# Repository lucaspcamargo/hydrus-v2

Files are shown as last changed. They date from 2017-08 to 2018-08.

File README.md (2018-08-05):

# Hydrus v2

Hydrus is an autonomous surface vehicle for water quality measurement. The original v1 platform won **first place at the Intel Embedded Systems Competition 2016**. This repository contains v2: a ground-up retool of the vehicle firmware and hardware, now running on a **Raspberry Pi Zero W** atop a custom backbone board.

The vehicle navigates a body of water along a pre-planned route, stops at designated waypoints to collect sensor readings, and streams data in real time to a Qt5-based base station running on a laptop.

The project spans embedded firmware, base station software, custom PCB hardware design, and 3D-printed mechanical components.

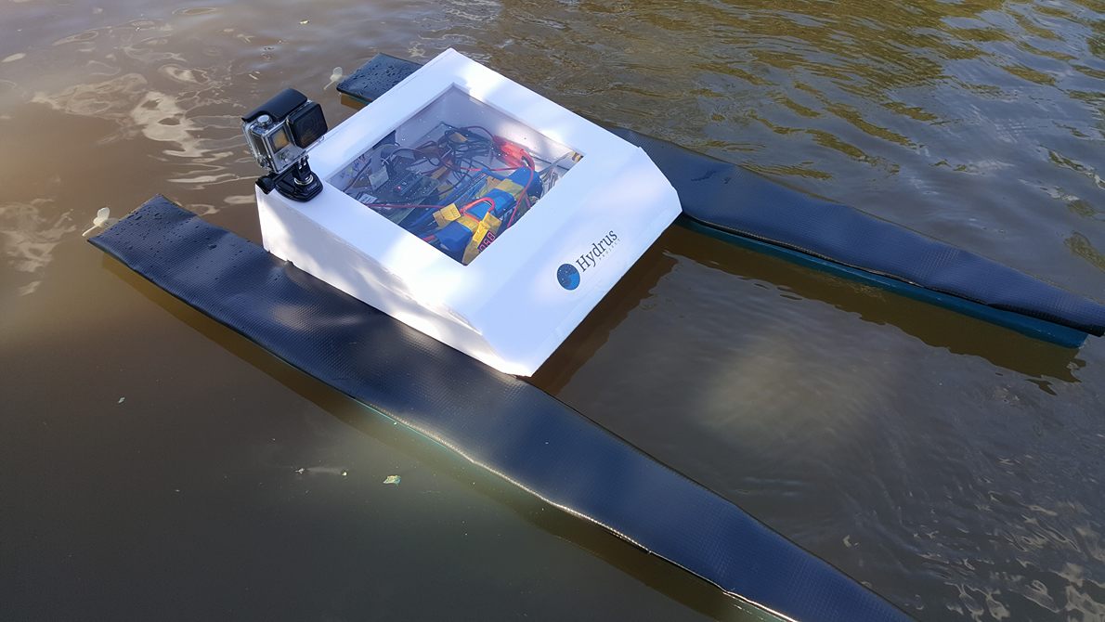
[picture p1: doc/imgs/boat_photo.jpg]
Hydrus on the water


`Hydrus during field testing on a lake in Joinville, 2016.`

## Hardware

The vehicle runs on a Raspberry Pi Zero W with a custom backbone board that integrates all peripherals:

- **GPS**: u-blox NEO-6 for position and speed
- **IMU**: HMC5883L 3-axis magnetometer for heading
- **ADC**: ADS1115 16-bit I2C ADC multiplexing four analog channels
- **Water sensors**: pH probe, TMP36 temperature sensor, TSD-10 turbidity sensor
- **Propulsion**: dual brushed motors with PWM speed control (differential drive)
- **Power**: LiPo battery with voltage monitoring

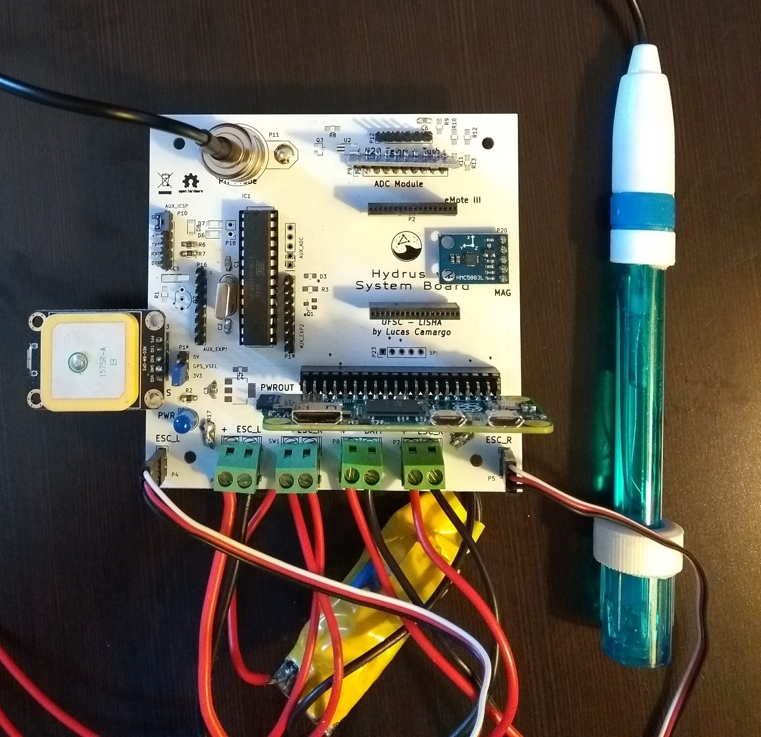
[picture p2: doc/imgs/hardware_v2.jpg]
Custom Hydrus System Board with GPS antenna and pH probe


`The custom Hydrus v2 System Board, with GPS antenna and pH probe.`

Hardware design files (KiCad schematics and layouts) are in `hw/`. Mechanical parts (propellers, axle adapters, board mounts) are 3D-printable models in `mech/`.

## Firmware

The vehicle firmware (`fw/`) is written in C++11 and built with CMake. It runs four concurrent periodic tasks:

| Task | Rate | Responsibility |
|------|------|----------------|
| `SystemTask` | 2 Hz | State machine, battery/thermal monitoring, shutdown |
| `SensingTask` | 30 Hz | pH, temperature, turbidity, IMU heading |
| `NavigationTask` | 10 Hz | GPS, motor control, waypoint tracking |
| `CommTask` | 20 Hz | TCP link to base station, command routing |

All tasks share a **double-buffered blackboard** with reader-writer locking, which eliminates contention between producers and consumers without blocking.

### Navigation

Autonomous navigation follows a state machine: align to bearing → traverse toward waypoint → acquire data → advance to next waypoint. Distance and bearing use the Haversine formula and forward azimuth calculation against WGS-84 coordinates. Speed is throttled adaptively as the vehicle closes in on a waypoint.

A remote-control mode is also supported, accepting velocity vectors from the base station for manual operation.

## Base Station

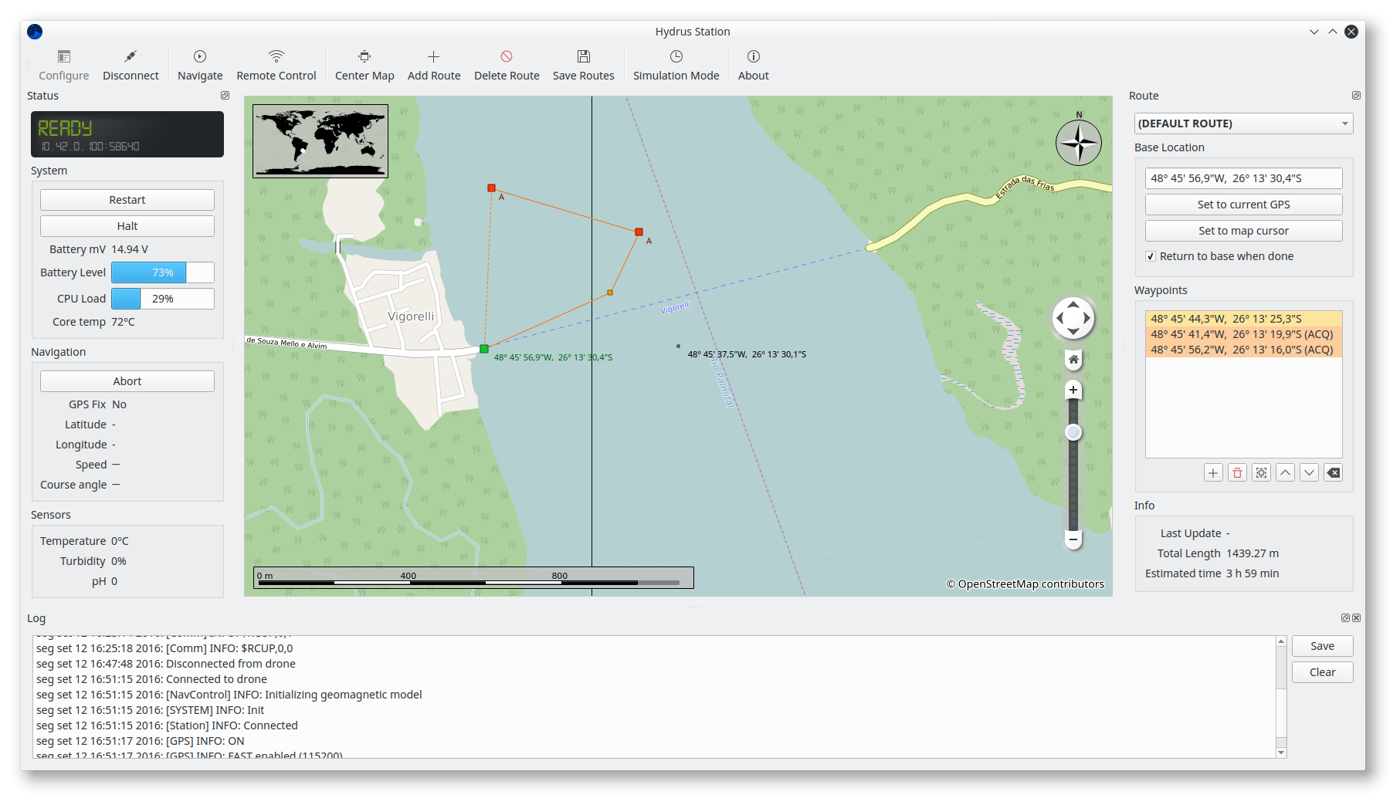
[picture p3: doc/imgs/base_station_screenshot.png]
Base station software showing a live mission on the map


`Base station software showing a live mission on the map.`

The base station (`station/`) is a Qt5/C++ desktop application featuring:

- **Live map** via the Marble widget, showing vehicle position, heading, trail, and waypoints over OpenStreetMap tiles
- **Route editor** for building multi-waypoint missions with per-waypoint acquire flags
- **Real-time dashboard** for sensor readings, system state, and battery level
- **Log viewer** with streaming from the vehicle and timeline-based replay
- **RC control widget** with joystick/gamepad support

Communication uses a TCP socket (port 6666). The vehicle streams binary blackboard snapshots and log messages; the base station sends text commands.

## Repository layout

```
doc/      Documentation and branding (including competition presentation)
fw/       Vehicle firmware (C++11, CMake)
lib/      Shared libraries
station/  Base station software (Qt5, C++11)
hw/       PCB schematics and layouts (KiCad)
mech/     3D-printable mechanical components
```

## Credits

The original Hydrus project was developed at Universidade Federal de Santa Catarina. Team members: Guilherme Augusto Pangratz and Emili Bohrer. Mentored by Prof. Dr. Giovani Gracioli.

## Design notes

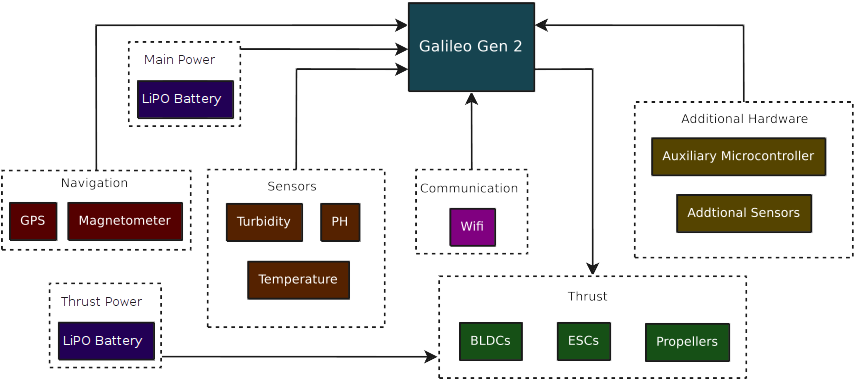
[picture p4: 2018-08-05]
doc/imgs/v1_hardware_blocks.png

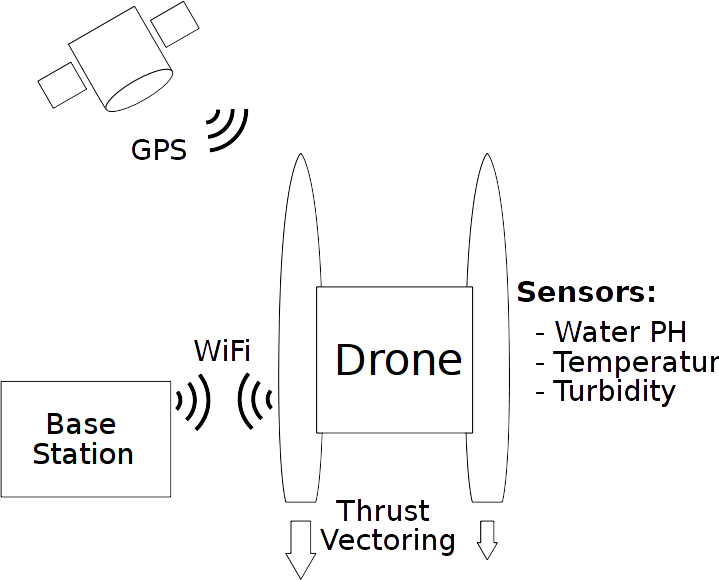
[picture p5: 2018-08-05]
doc/imgs/concept.png

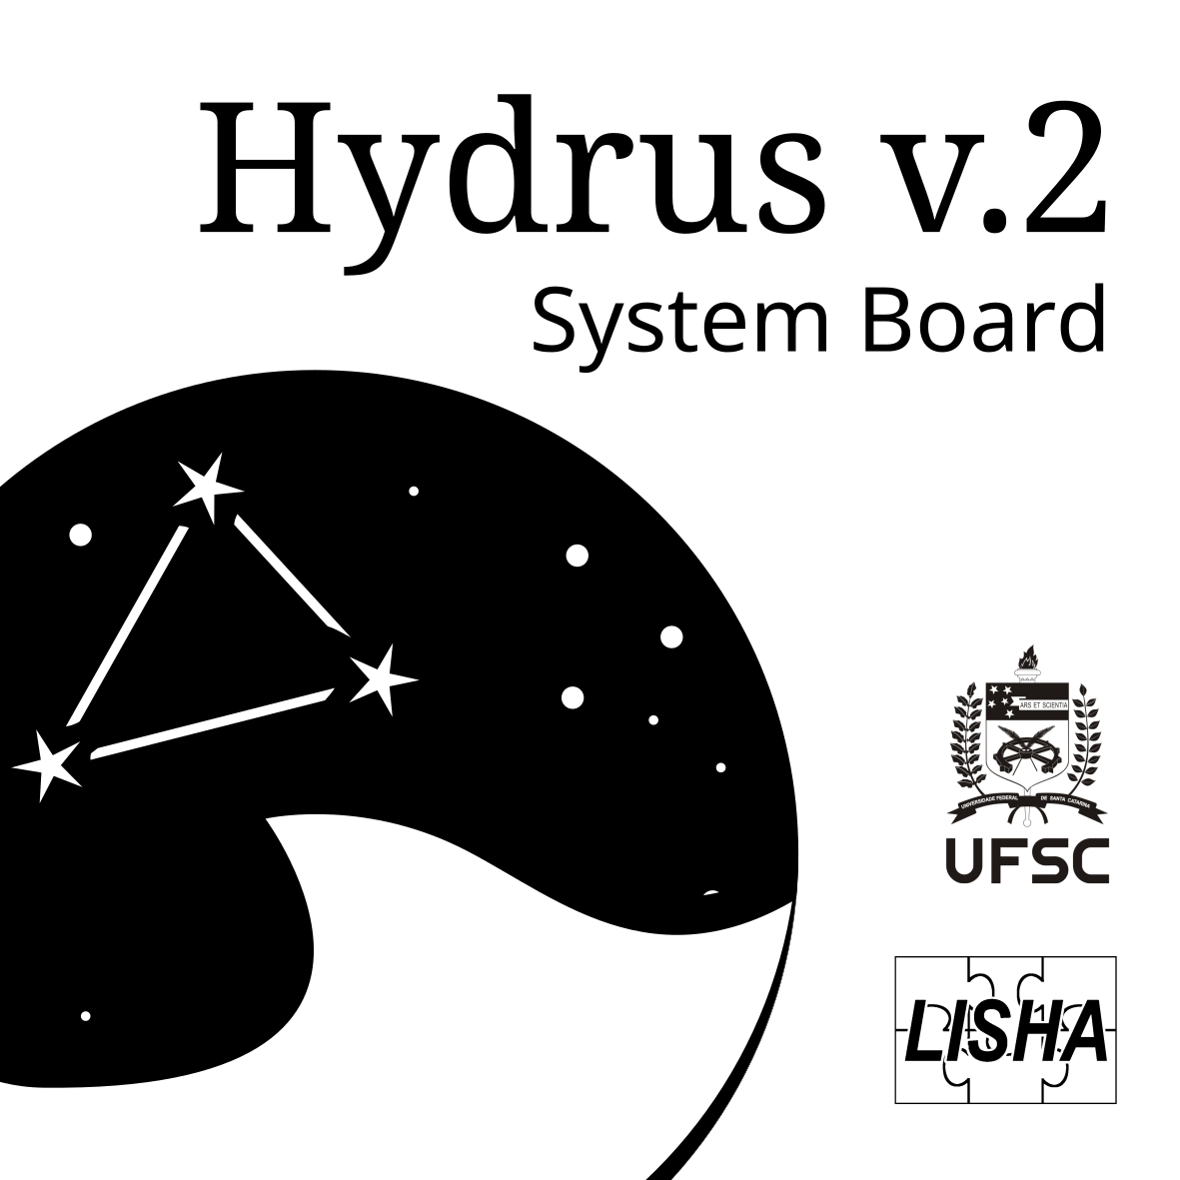
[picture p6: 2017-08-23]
doc/branding/board-backside.png

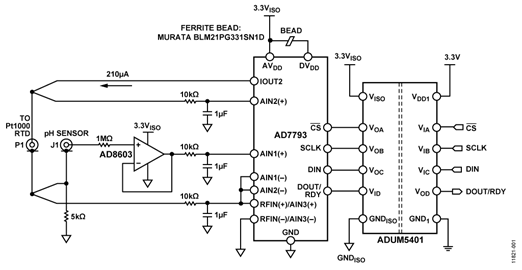
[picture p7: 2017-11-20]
hw/datasheets/ph-buffer-reference.png

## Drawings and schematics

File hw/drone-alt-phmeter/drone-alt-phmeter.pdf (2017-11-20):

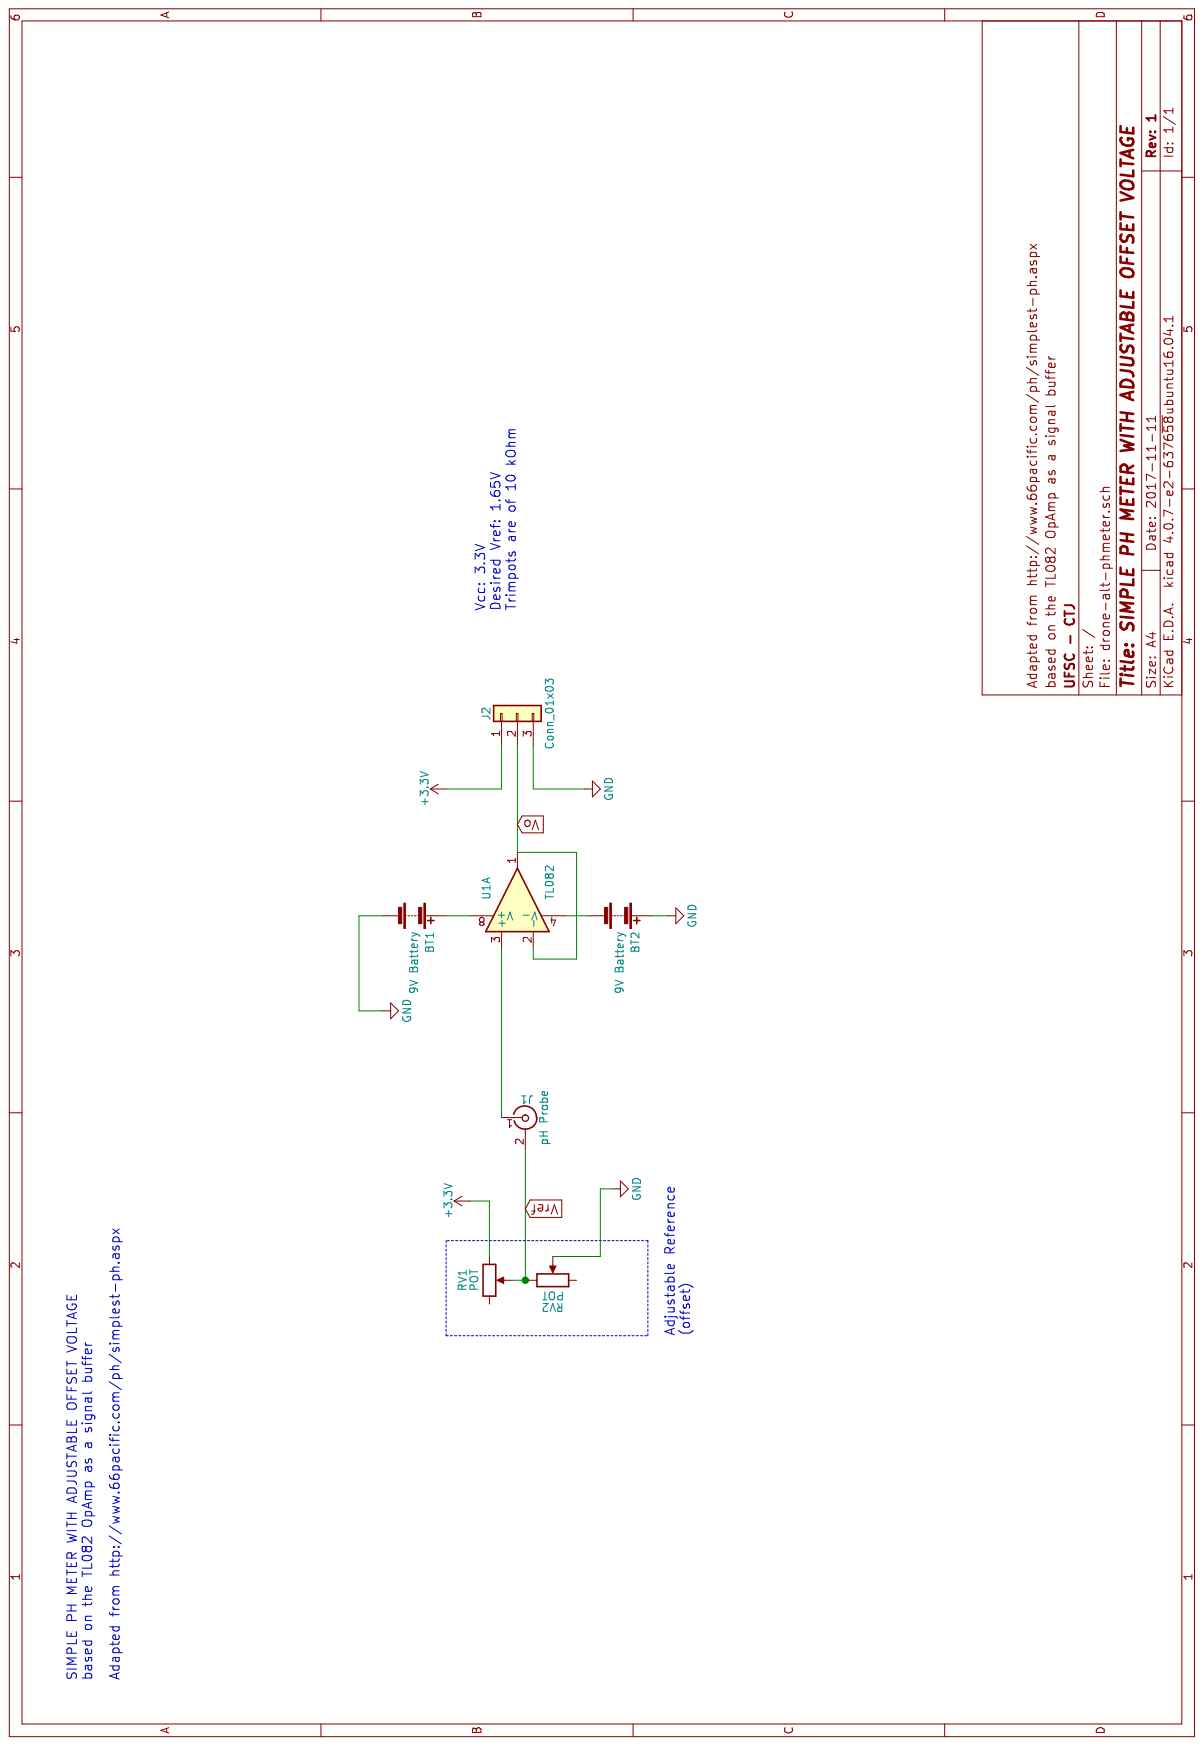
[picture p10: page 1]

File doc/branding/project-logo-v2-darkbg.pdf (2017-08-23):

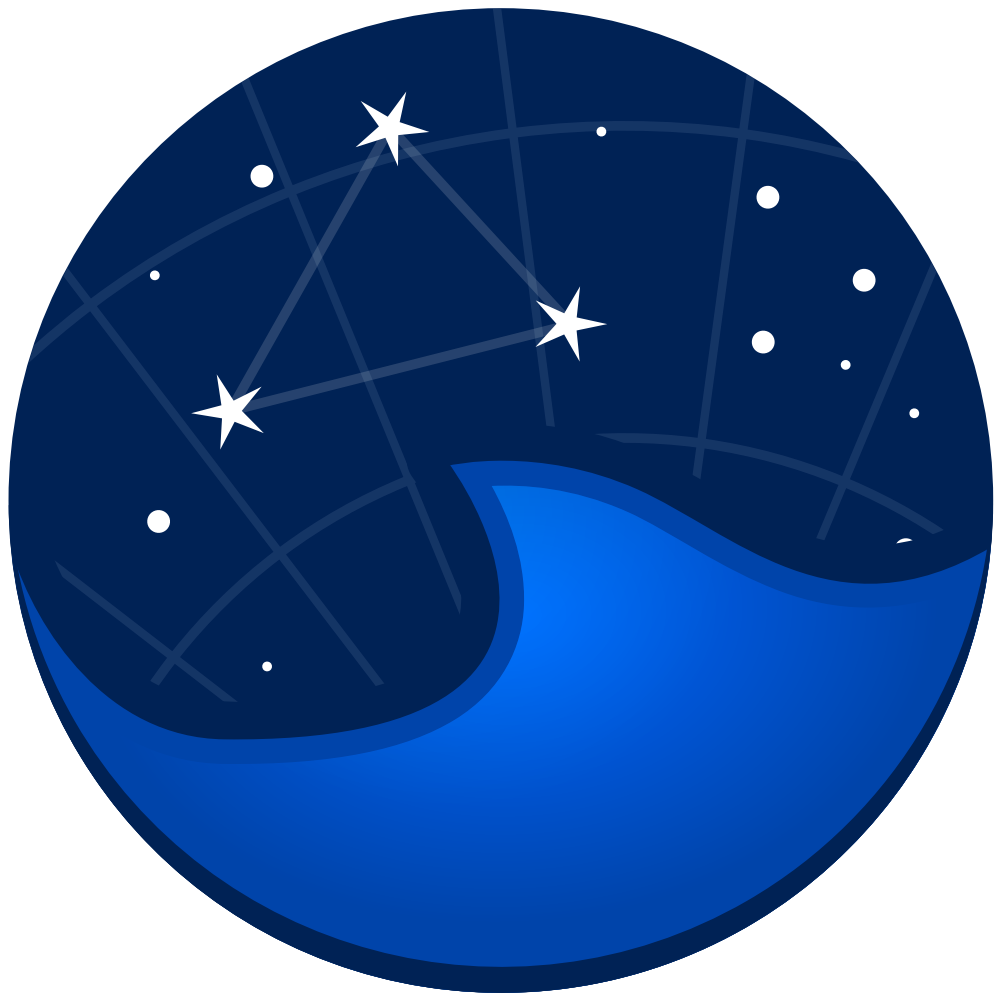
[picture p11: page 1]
Hydrus P R O J E C T

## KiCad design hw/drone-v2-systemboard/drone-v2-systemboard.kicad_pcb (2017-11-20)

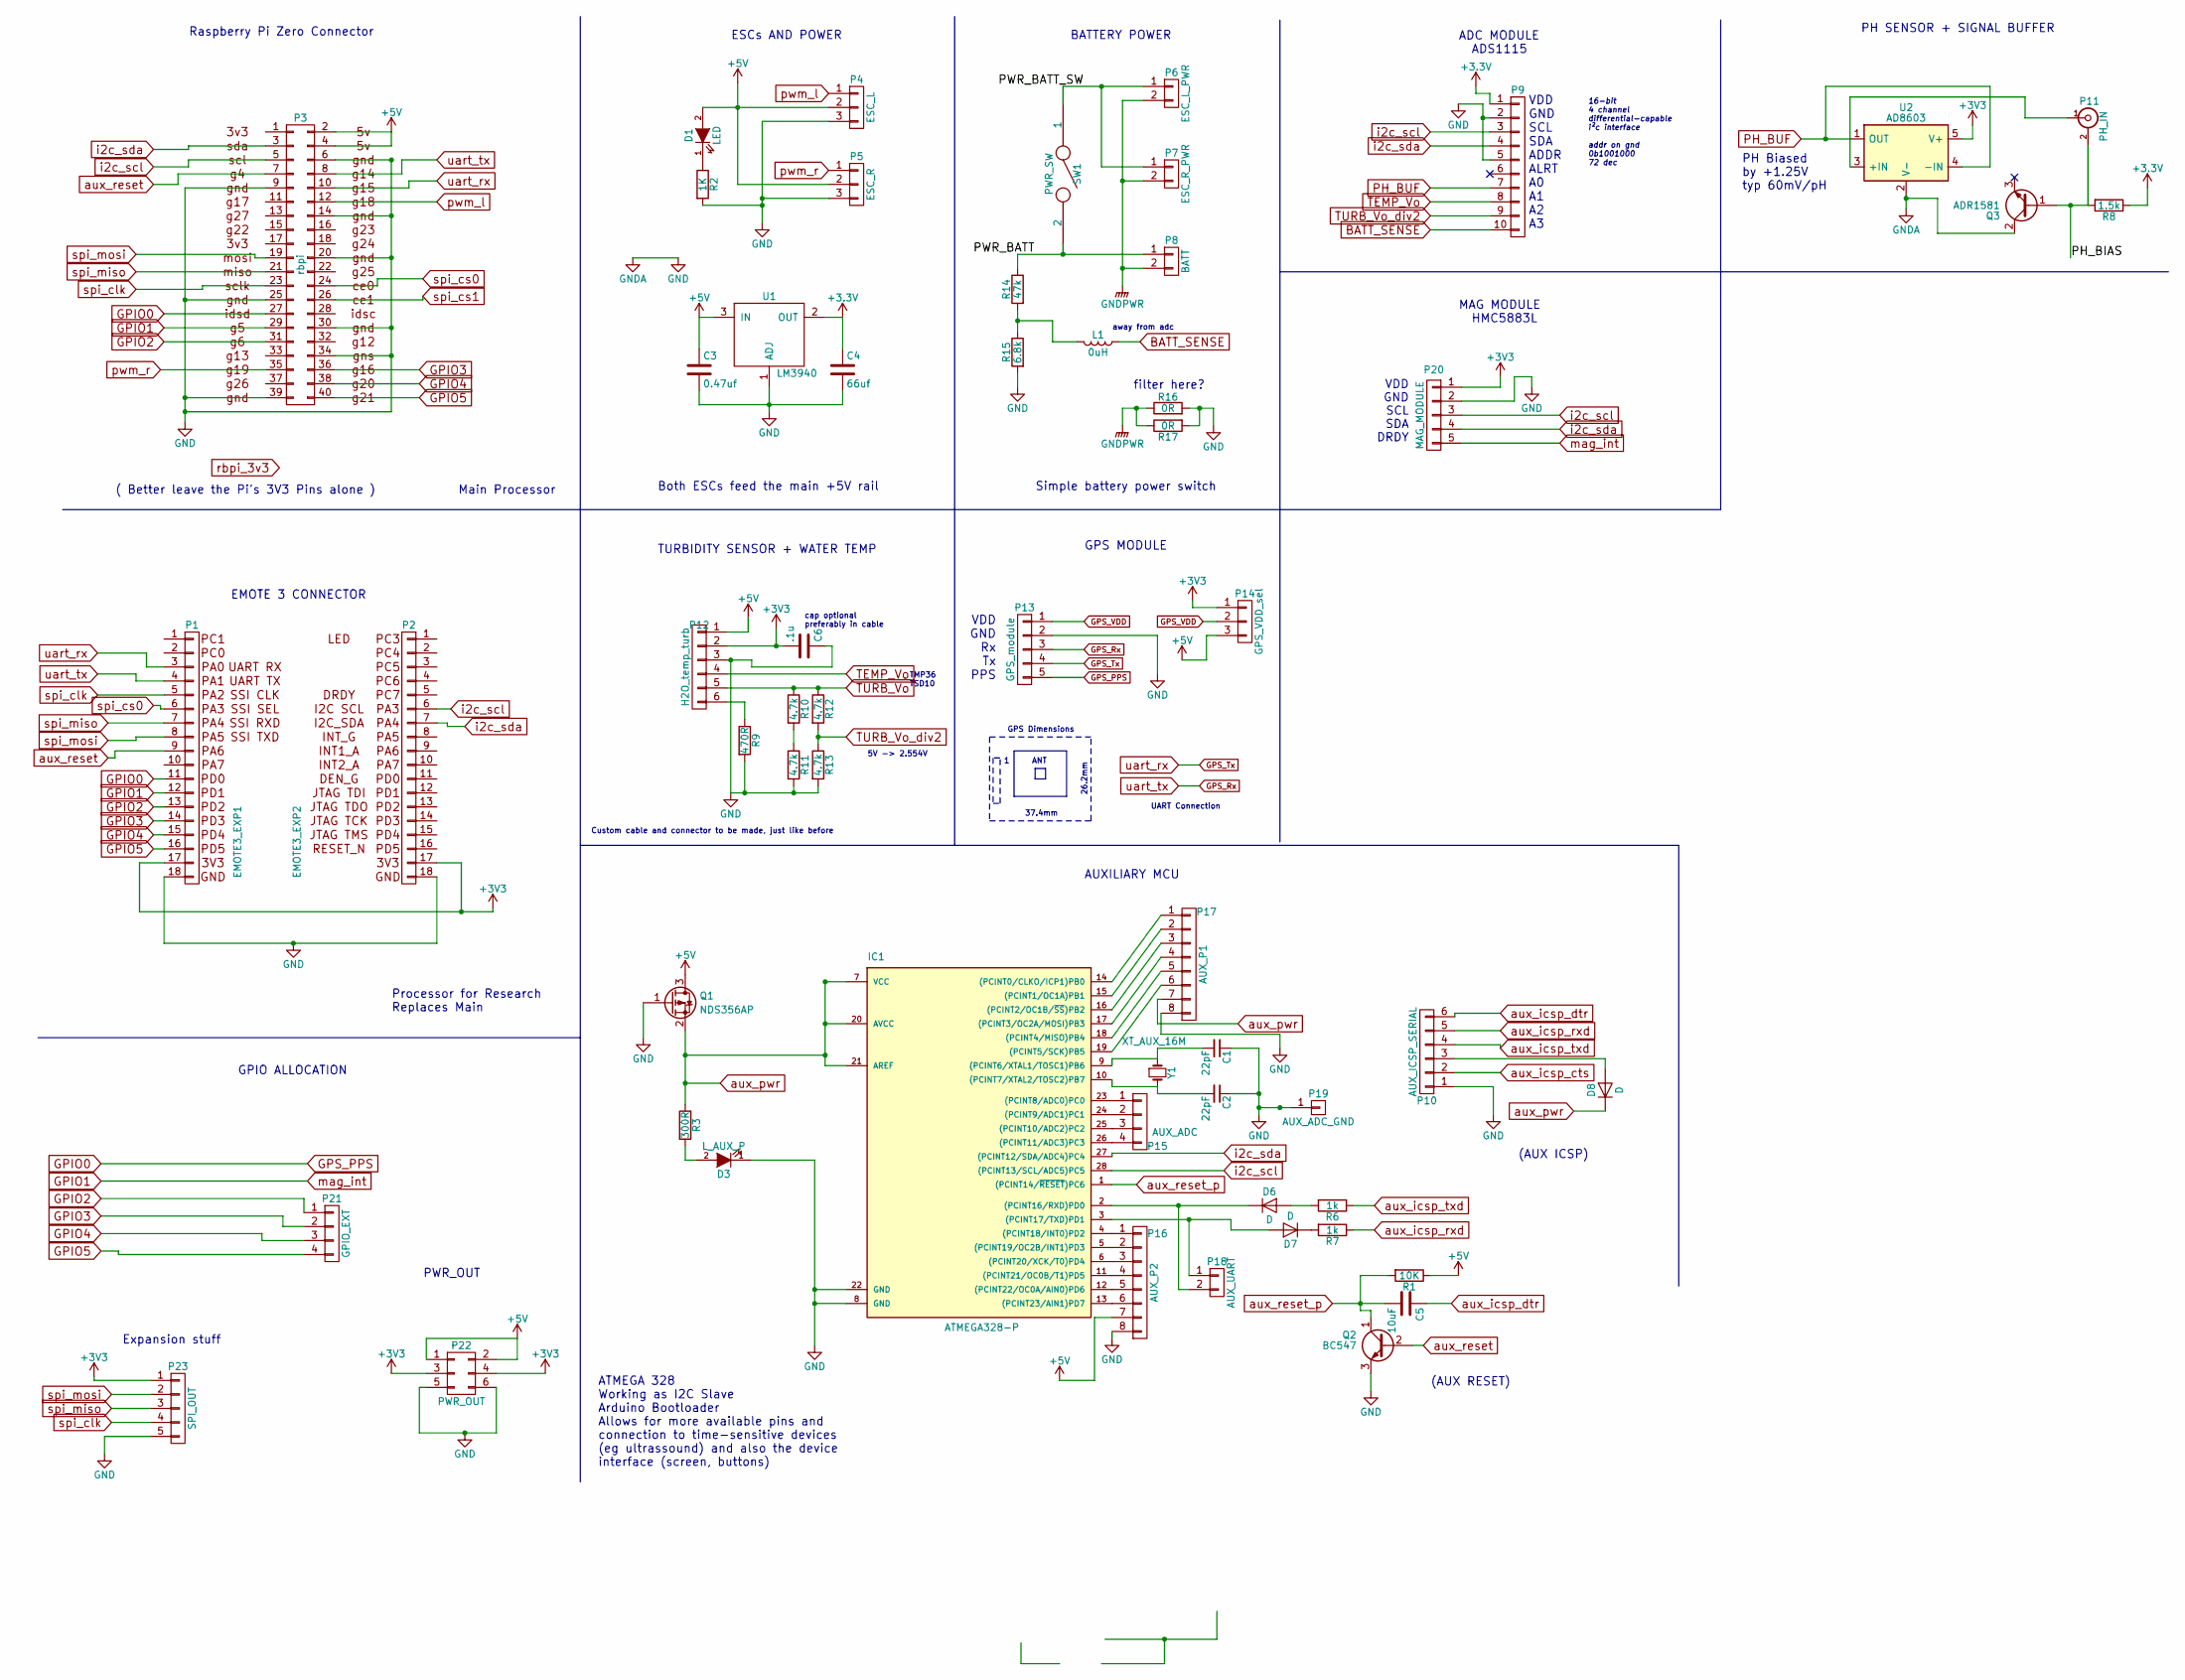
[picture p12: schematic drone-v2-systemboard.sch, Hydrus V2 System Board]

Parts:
C1, C2: 22pF; C_0805_HandSoldering
C3: 0.47uf; C_0805_HandSoldering
C4: 66uf; C_0805_HandSoldering
C5: 10uF; CP_Tantalum_Case-S_EIA-3216-12_Hand
C6: .1u; C_0805_HandSoldering
D1: LED; LED-5MM
D3: L_AUX_P; LED_0805
D6, D7, D8: D; D_SOD-123
IC1: ATMEGA328-P; DIP-28_W7.62mm
L1: 0uH; Inductor_1212
P1: EMOTE3_EXP1; HEADER_18x1_EMOTE
P2: EMOTE3_EXP2; HEADER_18x1_EMOTE
P3: rbpi; Pin_Header_Straight_2x20
P4: ESC_L; Pin_Header_Straight_1x03
P5: ESC_R; Pin_Header_Straight_1x03
P6: ESC_L_PWR; AK300-2
P7: ESC_R_PWR; AK300-2
P8: BATT; AK300-2
P9: ADC_MODULE; Pin_Header_Straight_1x10_Pitch2.54mm
P10: AUX_ICSP_SERIAL; Pin_Header_Straight_1x06_Pitch2.54mm
P11: PH_IN; BNC
P12: H2O_temp_turb; Pin_Header_Straight_1x06_Pitch2.54mm
P13: GPS_module; Pin_Header_Straight_1x05_Pitch2.54mm
P14: GPS_VDD_sel; Pin_Header_Straight_1x03_Pitch2.54mm
P15: AUX_ADC; Pin_Header_Straight_1x04_Pitch2.54mm
P16: AUX_P2; Pin_Header_Straight_1x08_Pitch2.54mm
P17: AUX_P1; Pin_Header_Straight_1x08_Pitch2.54mm
P18: AUX_UART; Pin_Header_Straight_1x02_Pitch2.54mm
P19: AUX_ADC_GND; Pin_Header_Straight_1x01_Pitch2.54mm
P20: MAG_MODULE; Pin_Header_Straight_1x05_Pitch2.54mm
P21: GPIO_EXT; Pin_Header_Straight_1x04_Pitch2.54mm
P22: PWR_OUT; Pin_Header_Straight_2x03_Pitch2.54mm
P23: SPI_OUT; Pin_Header_Straight_1x05_Pitch2.54mm
Q1: NDS356AP; SuperSOT-3
Q2: BC547; TO-92_Inline_Wide
Q3: ADR1581; SOT-23
R1: 10K; R_0805_HandSoldering
R2: 1K; R_0805_HandSoldering
R3: 300R; R_0805_HandSoldering
R6, R7: 1k; R_0805_HandSoldering
R8: 1.5k; R_0805_HandSoldering
R9: 470R; R_0805_HandSoldering
R10, R11, R12, R13: 4.7k; R_0805_HandSoldering
R14: 47k; R_0805_HandSoldering
R15: 6.8k; R_0805_HandSoldering
R16, R17: 0R; R_1210_HandSoldering
SW1: PWR_SW; AK300-2
U1: LM3940; SOT-223-3Lead_TabPin2
U2: AD8603; TSOT-23-5_HandSoldering
Y1: XT_AUX_16M; Crystal_HC49-U_Vertical

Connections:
+5V: C3.1, D1.2 (A), P3.2, P3.4, P4.2, P5.2, P12.1, P14.3, P16.7, P22.1, P22.2, Q1.3 (D), R1.1, U1.3 (IN)
/PH_BIAS: P11.2 (Ext), Q3.1 (B), R8.2
/PWR_BATT: P8.1, R14.1, SW1.2
/PWR_BATT_SW: P6.1, P7.1, SW1.1
BATT_SENSE: L1.1, P9.10
GND: C1.1, C2.1, C3.2, C4.2, C6.1, D3.1 (K), IC1.8 (GND), IC1.22 (GND), P1.18, P2.18, P3.6, P3.9, P3.14, P3.20, P3.25, P3.30, P3.34, P3.39, P4.3, P5.3, P9.2, P9.5, P10.1, P12.3, P13.2, P16.8, P17.8, P19.1, P20.2, P22.5, P22.6, P23.5, Q1.1 (G), Q2.3 (E), Q3.2 (C), R2.2, R9.2, R11.2, R13.2, R15.2, R16.2, R17.2, U1.1 (ADJ), U2.2 (V-)
GNDPWR: P6.2, P7.2, P8.2, R16.1, R17.1
GPIO0: P1.11, P3.27, P13.5
GPIO1: P1.12, P3.29, P20.5
GPIO2: P1.13, P3.31, P21.1
GPIO3: P1.14, P3.36, P21.2
GPIO4: P1.15, P3.38, P21.3
GPIO5: P1.16, P3.40, P21.4
GPS_Rx: P1.4, P3.8, P13.3
GPS_Tx: P1.3, P3.10, P13.4
GPS_VDD: P13.1, P14.2
unnamed: C1.2, IC1.9 ((PCINT6/XTAL1/TOSC1)PB6), Y1.1
unnamed: C2.2, IC1.10 ((PCINT7/XTAL2/TOSC2)PB7), Y1.2
unnamed: D1.1 (K), R2.1
unnamed: D3.2 (A), R3.2
unnamed: D6.1 (K), IC1.2 ((PCINT16/RXD)PD0), P18.2
unnamed: D6.2 (A), R6.2
unnamed: D7.1 (K), R7.2
unnamed: D7.2 (A), IC1.3 ((PCINT17/TXD)PD1), P18.1
unnamed: D8.2 (A), P10.3
unnamed: IC1.4 ((PCINT18/INT0)PD2), P16.1
unnamed: IC1.5 ((PCINT19/OC2B/INT1)PD3), P16.2
unnamed: IC1.6 ((PCINT20/XCK/T0)PD4), P16.3
unnamed: IC1.11 ((PCINT21/OC0B/T1)PD5), P16.4
unnamed: IC1.12 ((PCINT22/OC0A/AIN0)PD6), P16.5
unnamed: IC1.13 ((PCINT23/AIN1)PD7), P16.6
unnamed: IC1.14 ((PCINT0/CLKO/ICP1)PB0), P17.1
unnamed: IC1.15 ((PCINT1/OC1A)PB1), P17.2
unnamed: IC1.16 ((PCINT2/OC1B/~SS~)PB2), P17.3
unnamed: IC1.17 ((PCINT3/OC2A/MOSI)PB3), P17.4
unnamed: IC1.18 ((PCINT4/MISO)PB4), P17.5
unnamed: IC1.19 ((PCINT5/SCK)PB5), P17.6
unnamed: IC1.23 ((PCINT8/ADC0)PC0), P15.1
unnamed: IC1.24 ((PCINT9/ADC1)PC1), P15.2
unnamed: IC1.25 ((PCINT10/ADC2)PC2), P15.3
unnamed: IC1.26 ((PCINT11/ADC3)PC3), P15.4
unnamed: L1.2, R14.2, R15.1
unnamed: P11.1 (In), U2.3 (+IN)
unnamed: P12.6, R9.1
unnamed: R10.2, R11.1
PH_BUF: P9.7, U2.1 (OUT), U2.4 (-IN)
TEMP_Vo: P9.8, P12.4
TURB_Vo: P12.5, R10.1, R12.1
TURB_Vo_div2: P9.9, R12.2, R13.1
aux_icsp_dtr: C5.1, P10.6
aux_icsp_rxd: P10.5, R7.1
aux_icsp_txd: P10.4, R6.1
aux_pwr: D8.1 (K), IC1.7 (VCC), IC1.20 (AVCC), IC1.21 (AREF), P17.7, Q1.2 (S), R3.1
aux_reset: P1.9, P3.7, Q2.2 (B)
aux_reset_p: C5.2, IC1.1 ((PCINT14/~RESET~)PC6), Q2.1 (C), R1.2
i2c_scl: IC1.28 ((PCINT13/SCL/ADC5)PC5), P2.6, P3.5, P9.3, P20.3
i2c_sda: IC1.27 ((PCINT12/SDA/ADC4)PC4), P2.7, P3.3, P9.4, P20.4
pwm_l: P3.12, P4.1
pwm_r: P3.35, P5.1
spi_clk: P1.5, P3.23, P23.4
spi_cs0: P1.6, P3.24
spi_miso: P1.7, P3.21, P23.3
spi_mosi: P1.8, P3.19, P23.2

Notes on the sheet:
EMOTE 3 CONNECTOR
Raspberry Pi Zero Connector
ESCs AND POWER
BATTERY POWER
AUXILIARY MCU
ADC MODULE ADS1115
(AUX RESET)
(AUX ICSP)
PH SENSOR + SIGNAL BUFFER
Both ESCs feed the main +5V rail
Simple battery power switch
TURBIDITY SENSOR + WATER TEMP
Main Processor
Processor for Research Replaces Main
PH Biased by +1.25V typ 60mV/pH
VDD GND SCL SDA ADDR ALRT A0 A1 A2 A3
16-bit 4 channel differential-capable i²c interface addr on gnd 0b1001000 72 dec
filter here?
away from adc
GPIO ALLOCATION
TMP36 TSD10
GPS MODULE
VDD GND Rx Tx PPS
26.2mm
37.4mm
ANT
GPS Dimensions
Custom cable and connector to be made, just like before
5V -> 2.554V
cap optional preferably in cable
VDD GND SCL SDA DRDY
MAG MODULE HMC5883L
ATMEGA 328 Working as I2C Slave Arduino Bootloader Allows for more available pins and connection to time-sensitive devices (eg ultrassound) and also the device interface (screen, buttons)
UART Connection
PWR_OUT
Expansion stuff
( Better leave the Pi's 3V3 Pins alone )

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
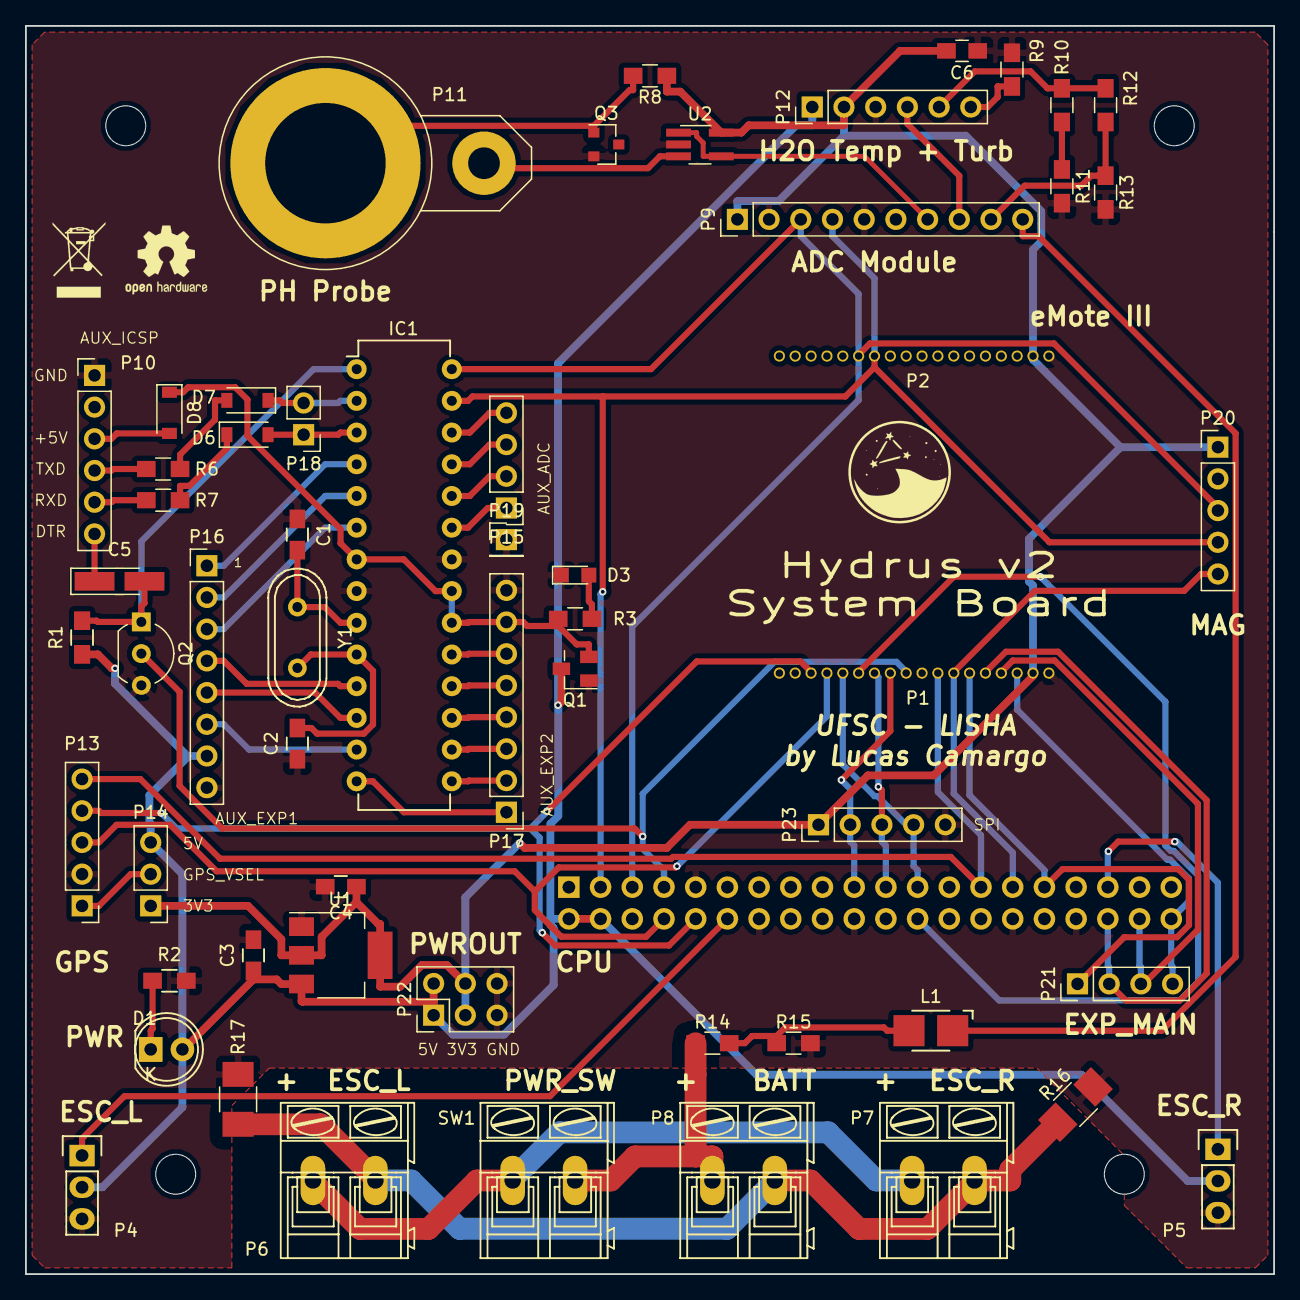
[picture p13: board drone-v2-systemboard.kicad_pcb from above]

Board: 2 copper layers, 100.0 x 100.0 mm, 64 parts (1 on the bottom side), 64 nets.

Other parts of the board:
HOLE1, HOLE2, HOLE3, HOLE4: MountingHole_3.2mm_M3_DIN965
oshwlogo: OSHW-Logo2_7.3x6mm_SilkScreen
weeelogo: WEEE-Logo_4.2x6mm_SilkScreen

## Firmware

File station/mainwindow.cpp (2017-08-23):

#include "mainwindow.h"
#include "ui_mainwindow.h"

#include <QScrollBar>
#include "droneconnection.h"
#include "serverconfigdialog.h"

#include "dronemap.h"
#include "droneroute.h"
#include "dronerouteset.h"
#include "droneblackboard.h"
#include "dronesimulator.h"
#include "dronelog.h"
#include "logtimelinewidget.h"

#include <marble/GeoDataCoordinates.h>
#include <QDateTime>



MainWindow::MainWindow(QWidget *parent) :
    QMainWindow(parent),
    ui(new Ui::MainWindow),
    m_logTimeline(0)
{
    ui->setupUi(this);
    ui->rcDock->setVisible(false);

    m_config = new ServerConfigDialog(this);

    m_mapWidget = new DroneMap(ui->mapContainer);
    m_currRoute = 0;

    m_routes = new DroneRouteSet(this);
    m_routes->restore();
    ui->routesCombo->setModel(m_routes);

    if(!m_routes->rowCount(QModelIndex()))
    {
        DroneRoute *r = m_routes->addRoute("(DEFAULT ROUTE)", -48.7658, -26.2251);
        r->setReturnHome(true);
        setCurrentRoute(r);
    }
    else
    {
        setCurrentRoute(m_routes->firstRoute());
    }

    // end bullshit test code

    QHBoxLayout *l = new QHBoxLayout;
    l->addWidget(m_mapWidget);
    l->setMargin(1);
    ui->mapContainer->setLayout(l);

    // restore settings
    restore();

    m_conn = new DroneConnection();
    connect(m_conn, &DroneConnection::connectedChanged, this , &MainWindow::handleConnectedChanged);
    connect(m_conn, &DroneConnection::logReceived, this , &MainWindow::appendLogMessage);
    connect(m_conn, &DroneConnection::blackboardChanged, this , &MainWindow::blackboardUpdate);
    connect(ui->statusDockContents, &StatusWidget::rebootClicked, m_conn, &DroneConnection::rebootDrone);
    connect(ui->statusDockContents, &StatusWidget::haltClicked, m_conn, &DroneConnection::haltDrone);
    connect(ui->statusDockContents, &StatusWidget::abortNavClicked, m_conn, &DroneConnection::abortDroneNavigation);
    handleConnectedChanged(false);

    connect(m_conn, &DroneConnection::connectedChanged, ui->statusDockContents , &StatusWidget::connectionUpdate);
    connect(m_conn, &DroneConnection::blackboardChanged, ui->statusDockContents , &StatusWidget::blackboardUpdate);


    connect(ui->actionRemote_Control, &QAction::toggled, ui->rcDockContents, &RCWidget::toggleRCMode);
    ui->rcDockContents->setDroneConnection(m_conn);

    m_sim = new DroneSimulator(this, m_conn);


}

MainWindow::~MainWindow()
{
    delete ui;
}

void MainWindow::handleConnectedChanged(bool conn)
{
    if(conn)
    {
        appendLogMessage("Connected to drone");
    }
    else
    {
        appendLogMessage("Disconnected from drone");
    }

    ui->statusDockContents->addressChanged(m_conn->host());

    ui->actionDisconnect->setEnabled(conn);
    ui->actionServer_Setup->setEnabled(!conn);

    ui->actionRemote_Control->setEnabled(conn);
    ui->actionRemote_Control->setChecked(false);
    ui->actionNavigate->setEnabled(conn);

    m_mapWidget->setDroneHasFix(false);
    m_mapWidget->setDroneLongitudeDeg(-48.7661);
    m_mapWidget->setDroneLatitudeDeg(-26.2248);

    ui->actionSimulation_Mode->setEnabled(conn);
}

void MainWindow::zoomCh(int)
{
}

void MainWindow::blackboardUpdate(Blackboard *bb)
{
    m_mapWidget->setDroneHasFix(bb->nav.gpsHasFix);
    m_mapWidget->setDroneLongitudeDeg(bb->nav.gpsLon);
    m_mapWidget->setDroneLatitudeDeg(bb->nav.gpsLat);
    m_mapWidget->setDroneHeadingDeg(bb->sys.state == SS_NAVIGATING? bb->nav.geoHeading : bb->sensors.imuHeading);
    m_mapWidget->update();
}

void MainWindow::appendLogMessage(const QString& text)
{
    bool scroll = ui->textEdit->verticalScrollBar()->value() == ui->textEdit->verticalScrollBar()->maximum();

    ui->textEdit->append(QDateTime::currentDateTime().toString() + ": " + text); // Adds the message to the widget

    if(scroll)
        ui->textEdit->verticalScrollBar()->setValue(ui->textEdit->verticalScrollBar()->maximum()); // Scrolls to the bottom
}

void MainWindow::on_actionDisconnect_triggered()
{
     m_conn->disconnect();
}

void MainWindow::setCurrentRoute(DroneRoute *r)
{
    m_currRoute = r;

    m_mapWidget->setRoute(m_currRoute);
    ui->routeWaypointsView->setModel(m_currRoute);

    ui->routeBaseLocation->setText(
                Marble::GeoDataCoordinates(m_currRoute->homeLongDeg(), m_currRoute->homeLatDeg(), 0.0, Marble::GeoDataCoordinates::Degree).toString());
    ui->routeReturnToBase->setChecked(m_currRoute->returnHome());

    updateRouteInfo();
}

#include <QTime>

void MainWindow::updateRouteInfo()
{
    if(m_currRoute)
    {
        qreal dist = m_currRoute->calculateTotalDistance();
        qreal estSecs = (dist/m_config->getDroneSpeedEstimate());
        int mins = (int)estSecs/60;

        ui->routeInfoLen->setText(QString("%1 m").arg(dist));
        if(mins < 60)
            ui->routeInfoEstTime->setText(QString("%1 min").arg(mins));
        else
            ui->routeInfoEstTime->setText(QString("%1 h %2 min").arg(mins/60).arg(mins - (mins/60)*60));
    }
    else
    {

    }
    m_mapWidget->update();
}

#include <QSettings>

void MainWindow::save()
{
    QSettings s;
    s.beginGroup("Main");

    s.setValue("centerLon", m_mapWidget->centerLongitude());
    s.setValue("centerLat", m_mapWidget->centerLatitude());
    s.setValue("zoom", m_mapWidget->zoom());
    s.setValue("currRouteIndex", ui->routesCombo->currentIndex());

    s.endGroup();
}

void MainWindow::restore()
{
    QSettings s;
    s.beginGroup("Main");

    m_mapWidget->setCenterLongitude(s.value("centerLon").toReal() ,Marble::Jump);
    m_mapWidget->setCenterLatitude(s.value("centerLat").toReal() ,Marble::Jump);
    m_mapWidget->setZoom(s.value("zoom").toInt() ,Marble::Jump);
    ui->routesCombo->setCurrentIndex(s.value("currRouteIndex").toInt());

    s.endGroup();
}


void MainWindow::on_logClearBtn_clicked()
{
    ui->textEdit->clear();
}

#include <QFileDialog>
#include <QFile>
void MainWindow::on_logSaveBtn_clicked()
{
    QString name = QFileDialog::getSaveFileName(this, "Save Log");
    if(name.isEmpty())
        return;

    QString log = ui->textEdit->toPlainText().append('\n');

    QFile file(name);
    file.open(QFile::WriteOnly);
    file.write(log.toLocal8Bit());
    file.close();
}

void MainWindow::on_actionServer_Setup_triggered()
{
    m_config->exec();
}

#include "aboutdialog.h"
void MainWindow::on_actionAbout_triggered()
{
    AboutDialog d(this);
    d.exec();
}

void MainWindow::on_actionCenter_Map_triggered()
{
    if(m_conn->connected())
    {
        if(m_conn->blackboard()->nav.gpsHasFix)
        {
            m_mapWidget->setCenterLatitude(m_conn->blackboard()->nav.gpsLat);
            m_mapWidget->setCenterLongitude(m_conn->blackboard()->nav.gpsLon);
        }
        else appendLogMessage("GPS has no fix. Can't center.");
    }
    else appendLogMessage("Not connected. Can't center.");
}

void MainWindow::on_routeReturnToBase_clicked()
{
    if(m_currRoute)
    {
        m_currRoute->setReturnHome(ui->routeReturnToBase->checkState() == Qt::Checked);
        updateRouteInfo();
    }
}

void MainWindow::on_routeSetStartCursor_clicked()
{
    if(m_currRoute)
    {
        m_currRoute->setHomeLatDeg(m_mapWidget->centerLatitude());
        m_currRoute->setHomeLongDeg(m_mapWidget->centerLongitude());
        updateRouteInfo();
    }
}

void MainWindow::on_routeSetStartGPS_clicked()
{
    if(m_conn->connected())
    {
        if(m_conn->blackboard()->nav.gpsHasFix)
        {
            m_mapWidget->setCenterLatitude(m_conn->blackboard()->nav.gpsLat);
            m_mapWidget->setCenterLongitude(m_conn->blackboard()->nav.gpsLon);
            m_currRoute->setHomeLatDeg(m_mapWidget->centerLatitude());
            m_currRoute->setHomeLongDeg(m_mapWidget->centerLongitude());
        }
        else appendLogMessage("GPS has no fix. Can't set home position.");
    }
    else appendLogMessage("Not connected. Can't set home position.");
}

#include <QInputDialog>

void MainWindow::on_actionAddRoute_triggered()
{
    QString name = QInputDialog::getText(this, "Route name", "Insert the name of the new route", QLineEdit::Normal);
    name = name.trimmed();
    if(!name.isEmpty())
    {
        if(name.contains(';'))
        {
            appendLogMessage("Route name cannot contain a semicolon \";\". Doing nothing.");
            return;
        }

        DroneRoute *r = m_routes->addRoute(name, m_mapWidget->centerLongitude(), m_mapWidget->centerLatitude());
        if(r)
            ui->routesCombo->setCurrentIndex(m_routes->routeIndex(name));
        else
            appendLogMessage(QString("Could not create route \"%1\".").arg(name));
    }
    else appendLogMessage("Route name not given. Doing nothing.");
}

void MainWindow::on_routesCombo_currentIndexChanged(const QString &arg1)
{
    if(arg1=="")
        ui->routesCombo->setCurrentIndex(0);
    else
        setCurrentRoute(m_routes->route(arg1));
}

void MainWindow::on_wayAdd_clicked()
{
    if(m_currRoute)
    {
        m_currRoute->addPoint(DroneRoute::Waypoint(m_mapWidget->centerLongitude(), m_mapWidget->centerLatitude(), false));
        updateRouteInfo();
    }
}

void MainWindow::on_wayDel_clicked()
{
    if(m_currRoute)
    {
        if(ui->routeWaypointsView->currentIndex().isValid())
        {
            m_currRoute->deletePoint(ui->routeWaypointsView->currentIndex().row());
            updateRouteInfo();
        }
    }
}

void MainWindow::on_waySet_clicked()
{
    if(m_currRoute)
    {
        if(ui->routeWaypointsView->currentIndex().isValid())
        {
            int idx = ui->routeWaypointsView->currentIndex().row();
            m_currRoute->updatePoint(idx, DroneRoute::Waypoint(m_mapWidget->centerLongitude(), m_mapWidget->centerLatitude(), m_currRoute->point(idx).acquire));
            updateRouteInfo();
        }
    }
}

void MainWindow::on_wayUp_clicked()
{
    if(m_currRoute)
    {
        if(ui->routeWaypointsView->currentIndex().isValid())
        {
            int idx = ui->routeWaypointsView->currentIndex().row();
            m_currRoute->movePointUp(idx);
            updateRouteInfo();
        }
    }
}

void MainWindow::on_wayDown_clicked()
{
    if(m_currRoute)
    {
        if(ui->routeWaypointsView->currentIndex().isValid())
        {
            int idx = ui->routeWaypointsView->currentIndex().row();
            m_currRoute->movePointDown(idx);
            updateRouteInfo();
        }
    }
}

void MainWindow::on_wayClear_clicked()
{
    if(m_currRoute)
    {
        m_currRoute->clear();
        updateRouteInfo();
        appendLogMessage("Route cleared");
    }
}

#include <QMessageBox>

void MainWindow::on_actionSave_Routes_triggered()
{
    int rep = QMessageBox::question(this, "Save", "Save current set of routes?", QMessageBox::Yes|QMessageBox::Default, QMessageBox::No|QMessageBox::Escape);
    if(rep == QMessageBox::Yes)
        m_routes->save();
}

void MainWindow::on_actionSimulation_Mode_changed()
{
    bool on = ui->actionSimulation_Mode->isChecked();

    if(on)
        m_sim->setDronePosition(m_mapWidget->centerLongitude(), m_mapWidget->centerLatitude());

    if(!m_sim->setActive(on))
        ui->actionSimulation_Mode->setChecked(false);
}

void MainWindow::on_actionNavigate_triggered()
{
    if(m_conn->connected())
    {
        if(m_currRoute)
        {
            //upload route to drone
            m_conn->sendCommand(QString("$NAVROUTE,%1").arg(m_currRoute->toCommand()));

            //send begin navigation
            m_conn->sendCommand("$NAVBEGIN");
        }

    }
    else appendLogMessage("Not connected. Doing nothing.");
}

void MainWindow::on_actionSend_Command_triggered()
{
    if(m_conn->connected())
    {
        QString cmd = QInputDialog::getText(this, "Command", "Insert manual command", QLineEdit::Normal, "$GPS,$PSRF104,-26.289961,-48.837110,0,96000,418383,1920,12,1*19");
        m_conn->sendCommand(cmd);

    }
}
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

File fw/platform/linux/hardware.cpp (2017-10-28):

#include <hydrus-config.h>

#include "platform/gpio.h"
#include "platform/serialport.h"
#include "platform/logger.h"

#include <sys/types.h>
#include <sys/stat.h>       
#include <unistd.h>
#include <sys/ioctl.h>
#include <fcntl.h>
#include <sys/termios.h>

#include <stdio.h>
#include <string.h>
#include <errno.h>


/* GPIO tables resolve a "platform" gpio number into a system-specific gpio number */
/* -1 means the pin is invalid  */
#define GPIO_TBL GPIO_DESKTOP_TBL

static const int8_t GPIO_DESKTOP_TBL[64] = {
    -1,  -1,  -1,  -1,  -1,  -1,  -1,  -1, 
    -1,  -1,  -1,  -1,  -1,  -1,  -1,  -1, 
    -1,  -1,  -1,  -1,  -1,  -1,  -1,  -1, 
    -1,  -1,  -1,  -1,  -1,  -1,  -1,  -1, 
    -1,  -1,  -1,  -1,  -1,  -1,  -1,  -1, 
    -1,  -1,  -1,  -1,  -1,  -1,  -1,  -1, 
    -1,  -1,  -1,  -1,  -1,  -1,  -1,  -1, 
    -1,  -1,  -1,  -1,  -1,  -1,  -1,  -1, 
};

static const int8_t GPIO_RBPI_TBL[64] = {
    -1,  -1,  -1,  -1,  -1,  -1,  -1,  -1, 
    -1,  -1,  -1,  -1,  -1,  -1,  -1,  -1, 
    -1,  -1,  -1,  -1,  -1,  -1,  -1,  -1, 
    -1,  -1,  -1,  -1,  -1,  -1,  -1,  -1, 
    -1,  -1,  -1,  -1,  -1,  -1,  -1,  -1, 
    -1,  -1,  -1,  -1,  -1,  -1,  -1,  -1, 
    -1,  -1,  -1,  -1,  -1,  -1,  -1,  -1, 
    -1,  -1,  -1,  -1,  -1,  -1,  -1,  -1, 
};


__HYDRUS_PLATFORM_BEGIN



// GPIO

struct GPIOPrivate
{
    int pin;
    GPIO::Direction dir;
    GPIO::Flags flags;
    
    GPIOPrivate( int syspin, GPIO::Direction direction, GPIO::Flags f)
    {
        pin = syspin;
        dir = direction;
        flags = f;
    }
};

GPIO::GPIO( unsigned int platformpin, Direction direction, Flags f )
{
    int8_t syspin = GPIO_TBL[platformpin];
    
    if( syspin < 0 )
    {
        _p = 0;
        P::Logger::log("gpio", "platform gpio has no system equivalent");
        return;
    }
    
    _p = new GPIOPrivate( syspin, direction, f );
    
    int expfd = open("/sys/class/gpio/export", O_WRONLY);
    if (-1 == expfd) 
    {    
        P::Logger::log("gpio", "failed to export gpio");
        _p = 0;
        return;
    }
    
    char expbuf[4];
    int expcount = snprintf(expbuf, 4, "%d", syspin);
    if(expcount != write(expfd, expbuf, expcount))
    {
        P::Logger::log("gpio", "failed to export gpio?");        
    }
    close( expfd );
    
    configure( direction, f );    
}
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

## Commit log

2017-08-23 First port components
    [axle-adapter.stl, galileo-support.stl, mpcie-adapter.stl, propeller-original.stl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]
2017-09-01 [threading] fixed wrong initialization
2017-10-28 [linux] corrected serial devices, do not use MCL_ONFAULT on arm
2017-10-28 [linux] fixed serial device again, added util
2017-10-28 [linux] added initial i2c implementation [magnetometer] device added
2017-10-28 [gps] added debug print trait
2017-10-29 [dev-mag] fix not setting device addr before read
2017-10-30 Most of functionality reinstated. Connection to station, pwm, motor control, navigation task, etc
2017-11-05 [traits] made motor factors equal
2017-11-05 [motors,pwm] added clamps
2017-11-05 [motors] missing header
2017-11-05 adc debug print
2017-11-05 [i2c] uses pigpio on raspberry pi
2017-11-07 [adc] give correct volts output
2017-11-11 [nav] added fixed magnetic declination setting [sensors] added classes
2017-11-11 [sensors] fixed battery voltage formula
2017-11-11 [adc] removed erroneous voltage scaling
2017-11-11 [adc] debug print
2017-11-11 [sensors] added filter to pH sensor converter
2017-11-11 [traits] fixed battery voltage divider resistor value
2017-11-20 [hw] added hardware project files
    [axle-adapter.stl, drone-alt-phmeter.kicad_pcb, drone-alt-phmeter.sch, drone-v2-systemboard-B.Cu.gbr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]
2017-11-20 removed mechanical files from hardware section
    [axle-adapter.stl, galileo-support.stl, mpcie-adapter.stl, propeller-original.stl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]
2017-11-20 [platform] added thread start function
2017-11-20 [ph] calibration mode
2017-11-20 [ph] calibrated
2017-11-20 [temp] calibrated
2017-11-20 [turb] calibrated
